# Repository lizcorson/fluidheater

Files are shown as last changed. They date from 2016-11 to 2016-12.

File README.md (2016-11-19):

# fluidheater
A small heater for flowing fluids.

## About
This is a project I'm working on for grad school. My goal is to heat flowing buffer fluid to skin temperature.

## Parts

* [Adafruit Feather 32u4 Basic Proto](http://www.digikey.com/product-search/en?keywords=1528-1514-ND)
* [Featherwing Proto](http://www.digikey.com/product-search/en?keywords=1528-1622-ND)
* [MOSFET](http://www.digikey.com/product-search/en?keywords=IRLB8721PBF-ND)
* [MAX31855 board](http://www.digikey.com/product-search/en?keywords=1528-1000-ND)
* [5V DC adapter](http://www.digikey.com/product-search/en?keywords=237-1385-ND)
* [Panel mount DC jack](http://www.digikey.com/product-search/en?keywords=CP-5-ND)
* [UM232R board](http://www.mouser.com/ProductDetail/FTDI/UM232R/)
* Male and female headers
* 1k resistor
* [Nichrome resistance heating wire, 30 AWG, p/n NI60-10-50](http://www.omega.com/pptst/NI60.html)
* [Type K 30 AWG thermocouple from Omega, SC-TT-K-30-36](http://www.omega.com/pptst/5LSC_5SRTC.html)
* [1/8" OD stainless tube (McMaster-Carr p/n 89895K712)](https://www.mcmaster.com/#catalog/122/148/=14vfa54)
* Swagelok fittings: 2x 1/16" port connector (SS-101-PC), 2x 1/8" to 1/16" reducing union (SS-200-6-1)

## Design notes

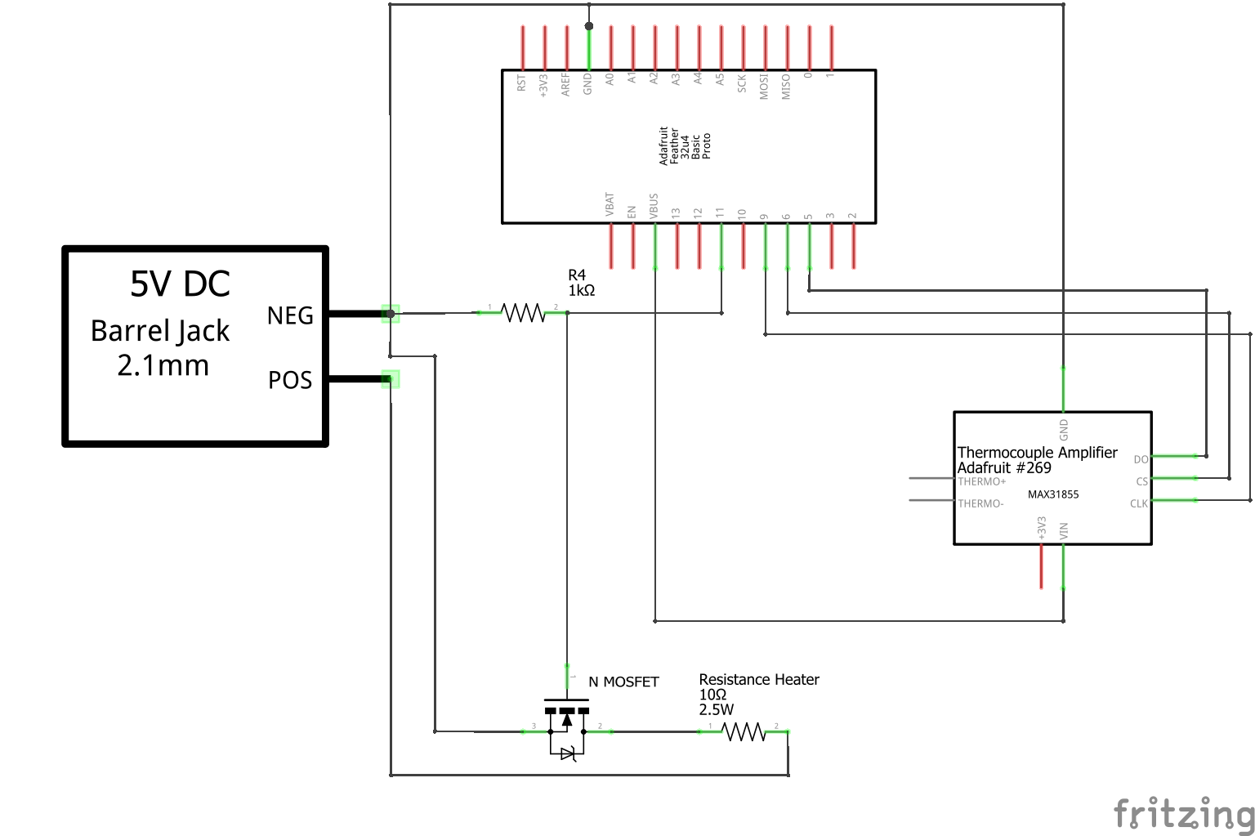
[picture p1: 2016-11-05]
schematics/heater schematic.png

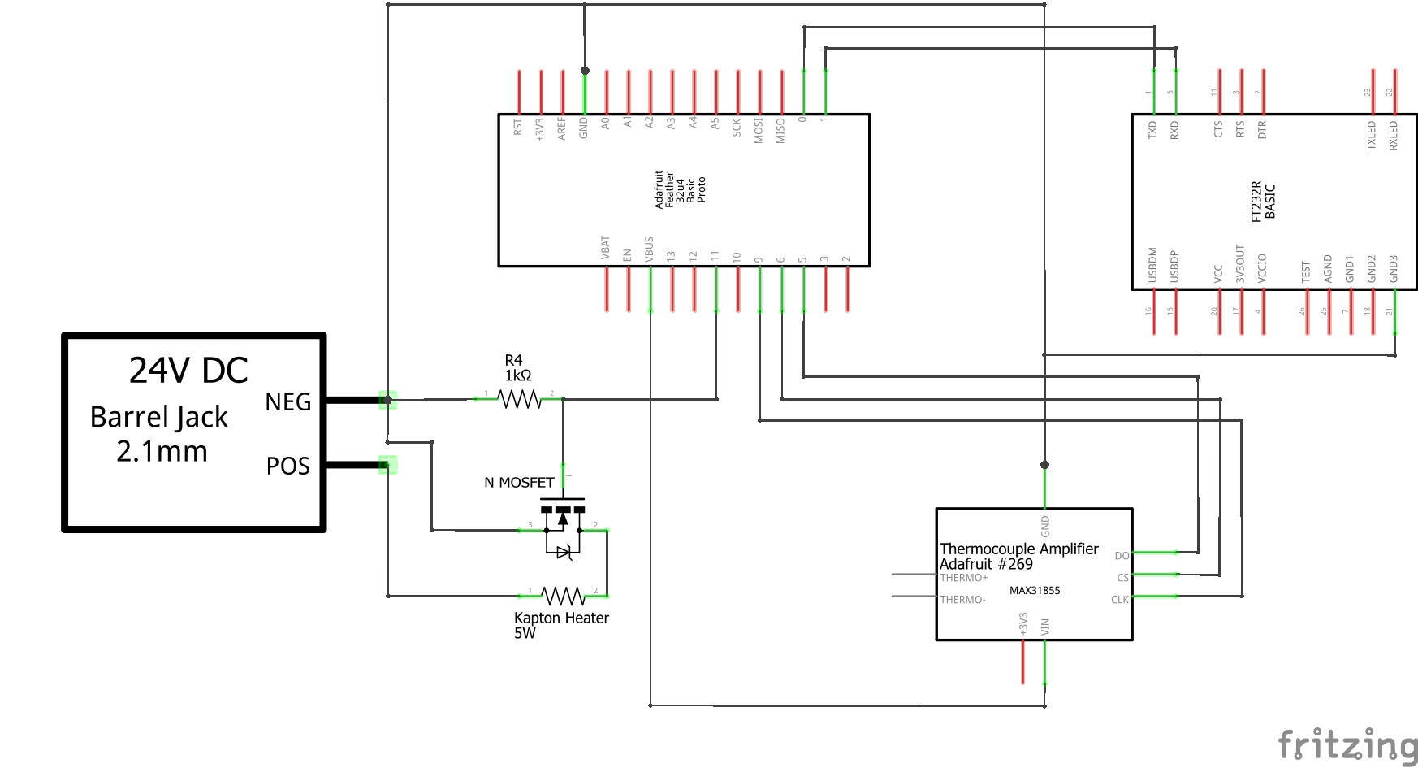
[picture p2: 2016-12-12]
schematics/heater schematic - kapton heater.png

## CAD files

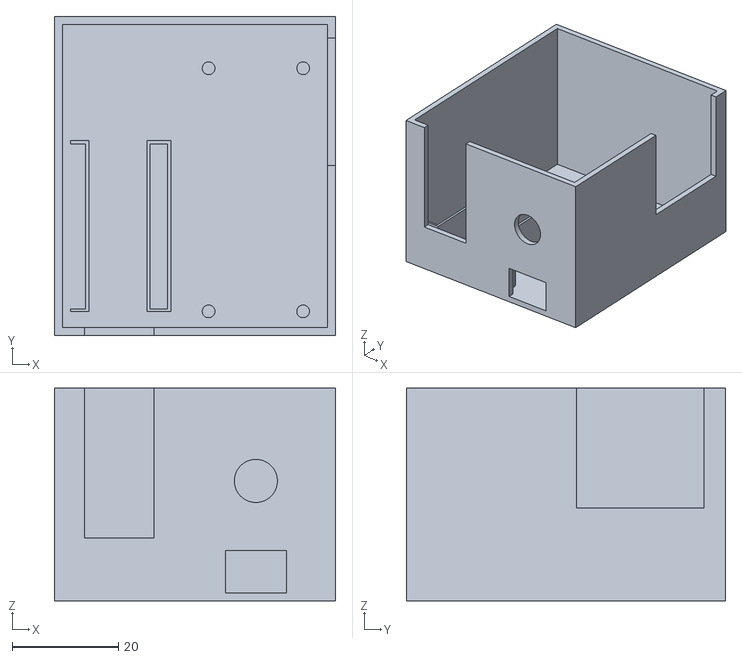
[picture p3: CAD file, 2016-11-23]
3dmodels/new case bottom.stl
52.9 x 60.0 x 40.0

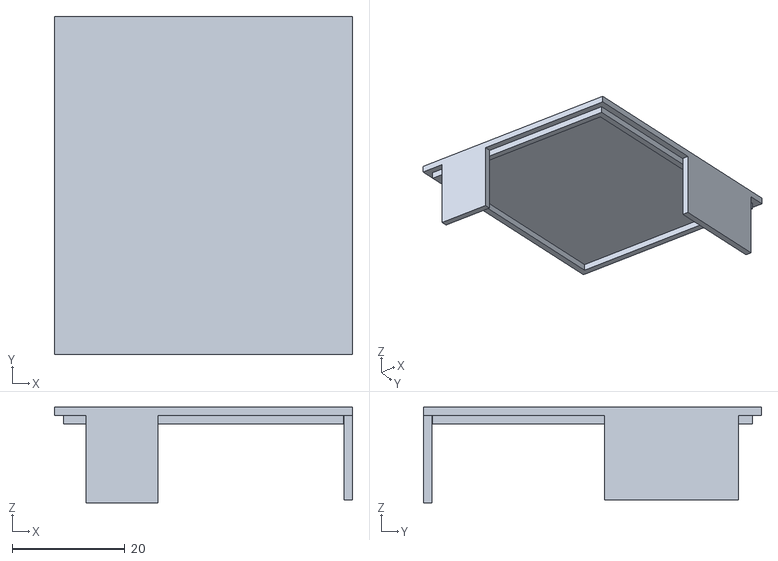
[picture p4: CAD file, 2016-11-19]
3dmodels/new case top.stl
52.9 x 60.0 x 17.0

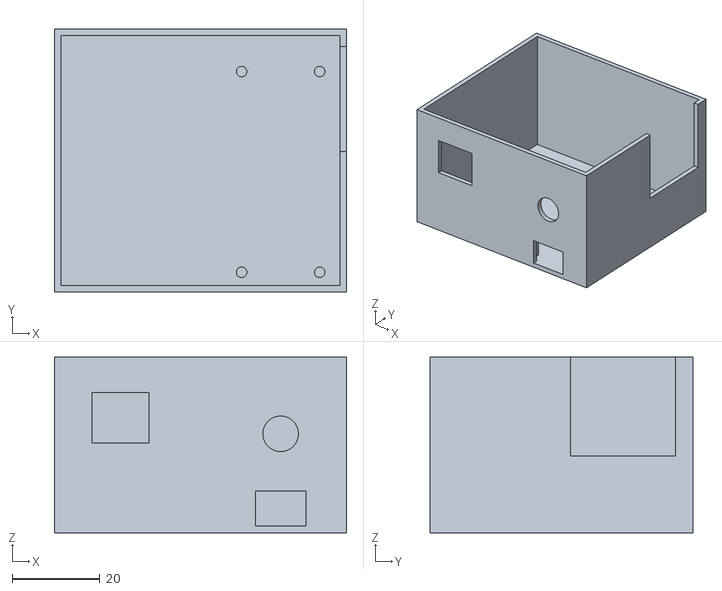
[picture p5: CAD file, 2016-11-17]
3dmodels/wide case bottom.stl
66.5 x 60.0 x 40.0

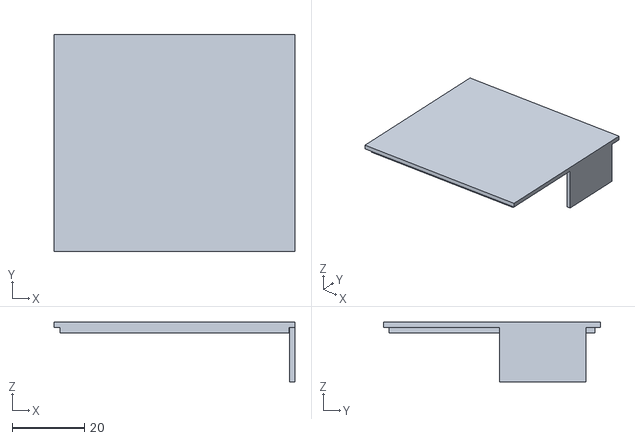
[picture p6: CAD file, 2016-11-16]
3dmodels/wide case top.stl
66.5 x 60.0 x 16.5

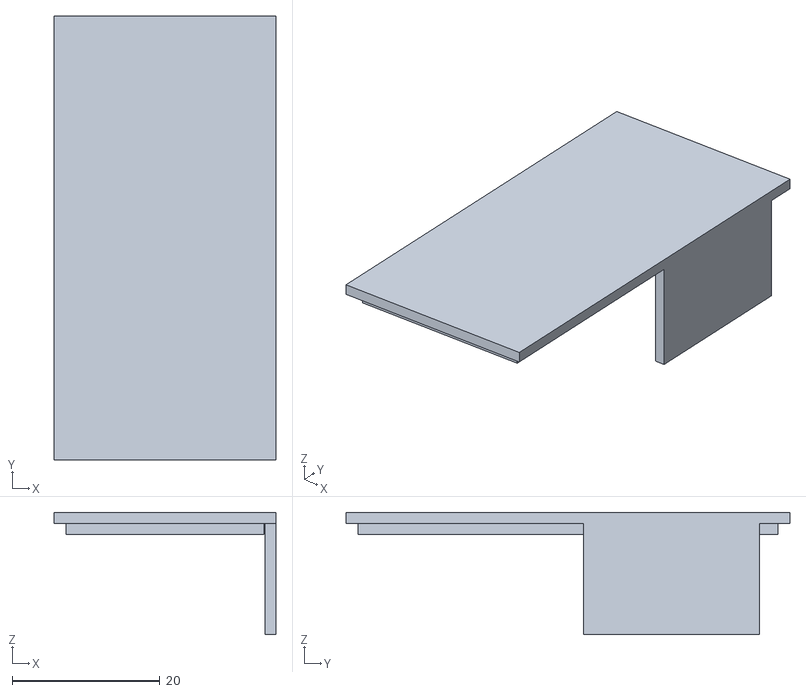
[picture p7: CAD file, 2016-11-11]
3dmodels/heater case top.stl
30.0 x 60.0 x 16.5

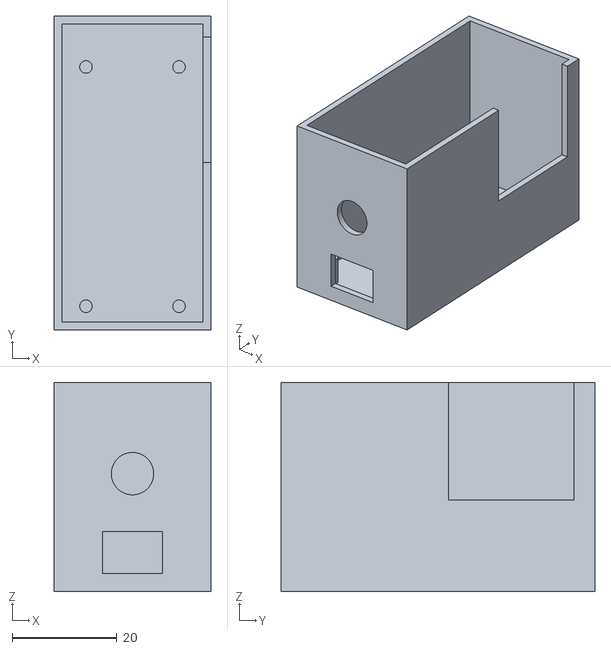
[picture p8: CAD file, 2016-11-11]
3dmodels/heater case bottom.stl
30.0 x 60.0 x 40.0

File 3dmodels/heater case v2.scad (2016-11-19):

wallthick = 1.5;

peg_r = 2.4/2;
peg_placelow = 0;
peg_placehigh = peg_placelow + 45.72;
fnval = 100;
peg_h = 6;
peg_spread = 17.78;

case_bottom_width = 30;
case_bottom_depth = 60;
case_bottom_height = 40;

pegs_xtranslate = (case_bottom_width-peg_spread)/2;
//pegs_ytranslate = 
//pegs_ztranslate = 

feather_depth = 50.8;
feather_width = 22.86;
feather_height = 1;

feather_xtranslate = (case_bottom_width-feather_width)/2;
feather_ytranslate = wallthick+.5;
feather_ztranslate = wallthick+1;


tc_cutout_xtranslate = case_bottom_width-wallthick;
tc_cutout_ytranslate = feather_ytranslate+30;
tc_cutout_ztranslate = wallthick+16;


tc_cutout_width = wallthick;
tc_cutout_depth = 24;
tc_cutout_height = case_bottom_height-tc_cutout_ztranslate;

tc_cover_height = 15;

usb_width = 11.5;
usb_height = 8;
usb_depth = wallthick;

usb_xtranslate = (case_bottom_width-usb_width)/2;
usb_ytranslate = 0;
usb_ztranslate = wallthick;

dcjack_r = 8.1/2;

dcjack_xtranslate = (case_bottom_width-2*dcjack_r)/2+dcjack_r;
dcjack_ytranslate = 0;
dcjack_ztranslate = feather_ztranslate+16+dcjack_r;

tolerance = .1;

boardwidth = 33.5;
boarddepth = 49;
boardheight = 1.2;
boardoffsety = 5;
usb2width = 13;
usb2height = 11.5;
usb2x = -15-usb2width;
usb2y = 0;
usb2z = 19+wallthick;

leftcasewidth = boardwidth + 3;
leftcasedepth = case_bottom_depth;
leftcaseheight = case_bottom_height;

*case_bottom();
case_top();

*translate([-boardwidth,boardoffsety,0]) cube([boardwidth,boarddepth,boardheight]);

module case_bottom() {
    union() {
        leftcase();
        rightcase();
    }
}

module leftcase() {
    difference () {
        translate([-leftcasewidth,0,0]) cube([leftcasewidth,leftcasedepth,leftcaseheight],center=false);
        translate([-leftcasewidth+wallthick,wallthick,wallthick]) cube([leftcasewidth-wallthick*2,leftcasedepth-wallthick*2,leftcaseheight],center=false);
        translate([-wallthick,wallthick,wallthick]) cube([wallthick,case_bottom_depth-wallthick*2,case_bottom_height]);
        translate([usb2x,usb2y,usb2z]) cube([usb2width,wallthick,usb2height]);
        
    }
}


module case_top() {
    //top
    translate([-leftcasewidth,0,case_bottom_height]) cube([case_bottom_width+leftcasewidth,case_bottom_depth,wallthick], center=false);
    
    //side panel
    translate([case_bottom_width-wallthick,tc_cutout_ytranslate+tolerance,case_bottom_height-tc_cover_height]) cube([wallthick,tc_cutout_depth-tolerance*2,tc_cover_height], center=false);
    
    //underneath
    translate([0,wallthick+tolerance,case_bottom_height-wallthick]) cube([case_bottom_width-wallthick-tolerance,case_bottom_depth-wallthick*2-tolerance*2,wallthick], center=false);
    translate([-leftcasewidth+wallthick+tolerance,wallthick+tolerance,case_bottom_height-wallthick]) cube([leftcasewidth-wallthick-tolerance,case_bottom_depth-wallthick*2-tolerance*2,wallthick], center=false);
}

module rightcase() {
    difference() {
        cube([case_bottom_width,case_bottom_depth,case_bottom_height], center=false);
        translate([wallthick,wallthick,wallthick]) cube([case_bottom_width-2*wallthick,case_bottom_depth-2*wallthick,case_bottom_height], center=false);
        translate([tc_cutout_xtranslate,tc_cutout_ytranslate,tc_cutout_ztranslate]) cube([tc_cutout_width,tc_cutout_depth,tc_cutout_height], center=false);
        translate([usb_xtranslate,usb_ytranslate,usb_ztranslate]) cube([usb_width, usb_depth, usb_height],center=false);
        translate([dcjack_xtranslate,dcjack_ytranslate,dcjack_ztranslate]) rotate([270,0,0]) cylinder(wallthick*1.1, dcjack_r, dcjack_r, false, $fn=fnval);
        translate([0,wallthick,wallthick]) cube([wallthick,case_bottom_depth-wallthick*2,case_bottom_height]);
    }
    translate([(case_bottom_width-peg_spread)/2,feather_ytranslate+2.54,0]) pegs();
}


*translate([feather_xtranslate,feather_ytranslate,feather_ztranslate]) feather();

module pegs() {
    translate([0,peg_placelow,wallthick])cylinder(peg_h, peg_r, peg_r, false, $fn=fnval);
    translate([peg_spread,peg_placelow,wallthick]) cylinder(peg_h, peg_r, peg_r, false, $fn=fnval);

    translate([0,peg_placehigh,wallthick])cylinder(peg_h, peg_r, peg_r, false, $fn=fnval);
    translate([peg_spread,peg_placehigh,wallthick]) cylinder(peg_h, peg_r, peg_r, false, $fn=fnval);
}

module feather() {
    cube([feather_width, feather_depth, feather_height], center = false);
}

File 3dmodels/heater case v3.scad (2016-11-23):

wallthick = 1.5;

peg_r = 2.4/2;
peg_placelow = 0;
peg_placehigh = peg_placelow + 45.72;
fnval = 100;
peg_h = 6;
peg_spread = 17.78;

case_bottom_width = 30;
case_bottom_depth = 60;
case_bottom_height = 40;

pegs_xtranslate = (case_bottom_width-peg_spread)/2;
//pegs_ytranslate = 
//pegs_ztranslate = 

feather_depth = 50.8;
feather_width = 22.86;
feather_height = 1;

um232_width = 17.9;
um232_depth = 38;
um232_height = 1.6;
um232_offset_x = -2;

u_usb_height = 10.7;
u_usb_width = 12;
u_usb_depth = 16.2;
u_usb_offset_y = -8;
u_usb_offset_x = 3.2;

uheader_height = 8.7;
uheader_depth = 30.2;
uheader_width = 2.5;
uheader_offset_y = 3.9;
uheader_offset_x1 = 0;
uheader_offset_x2 = um232_width - uheader_width;

feather_xtranslate = (case_bottom_width-feather_width)/2;
feather_ytranslate = wallthick+.5;
feather_ztranslate = wallthick+1;


tc_cutout_xtranslate = case_bottom_width-wallthick;
tc_cutout_ytranslate = feather_ytranslate+30;
tc_cutout_ztranslate = wallthick+16;


tc_cutout_width = wallthick;
tc_cutout_depth = 24;
tc_cutout_height = case_bottom_height-tc_cutout_ztranslate;

tc_cover_height = 15;

usb_width = 11.5;
usb_height = 8;
usb_depth = wallthick;

usb_xtranslate = (case_bottom_width-usb_width)/2;
usb_ytranslate = 0;
usb_ztranslate = wallthick;

dcjack_r = 8.1/2;

dcjack_xtranslate = (case_bottom_width-2*dcjack_r)/2+dcjack_r;
dcjack_ytranslate = 0;
dcjack_ztranslate = feather_ztranslate+16+dcjack_r;

tolerance = .1;

boardwidth = 33.5;
boarddepth = 49;
boardheight = 1.2;
boardoffsety = 5;
usb2width = 13;
usb2height = u_usb_height+(case_bottom_height-um232_height-uheader_height);
usb2x = -usb2width-u_usb_offset_x+um232_offset_x+1;
usb2y = 0;
usb2z = uheader_height+um232_height+wallthick;

leftcasewidth = um232_width + 5;
leftcasedepth = case_bottom_depth;
leftcaseheight = case_bottom_height;

module um232() {
    cube([um232_width,um232_depth,um232_height]);
    translate([u_usb_offset_x,u_usb_offset_y,um232_height]) cube([u_usb_width,u_usb_depth,u_usb_height]);
    translate([uheader_offset_x1,uheader_offset_y,-uheader_height]) cube([uheader_width,uheader_depth,uheader_height]);
    translate([uheader_offset_x2,uheader_offset_y,-uheader_height]) cube([uheader_width,uheader_depth,uheader_height]);
}

case_bottom();
*case_top();

shell_width = 1;
*translate([-um232_width+um232_offset_x,wallthick+tolerance,uheader_height+wallthick]) um232();

module um232holder() {
    difference() {
        color([1,0,0]) translate([um232_offset_x-um232_width+uheader_offset_x2-shell_width,uheader_offset_y+tolerance+wallthick-shell_width,wallthick]) cube([uheader_width+shell_width*2,uheader_depth+shell_width*2,uheader_height]);
        translate([uheader_offset_x2-um232_width+um232_offset_x-tolerance*4,uheader_offset_y+wallthick-tolerance*4,-uheader_height+uheader_height+wallthick]) cube([uheader_width+tolerance*8,uheader_depth+tolerance*8,uheader_height]);
    }
    difference() {
        color([1,0,0]) translate([um232_offset_x-um232_width+uheader_offset_x1,uheader_offset_y+tolerance+wallthick-shell_width,wallthick]) cube([uheader_width+shell_width,uheader_depth+shell_width*2,uheader_height]);
        translate([uheader_offset_x1-um232_width+um232_offset_x,uheader_offset_y+wallthick-tolerance*4,-uheader_height+uheader_height+wallthick]) cube([uheader_width+tolerance*4,uheader_depth+tolerance*8,uheader_height]); 
    }
}



*translate([-boardwidth,boardoffsety,0]) cube([boardwidth,boarddepth,boardheight]);

module case_bottom() {
    union() {
        leftcase();
        rightcase();
        um232holder();
    }
}

module leftcase() {
    difference () {
        translate([-leftcasewidth,0,0]) cube([leftcasewidth,leftcasedepth,leftcaseheight],center=false);
        translate([-leftcasewidth+wallthick,wallthick,wallthick]) cube([leftcasewidth-wallthick*2,leftcasedepth-wallthick*2,leftcaseheight],center=false);
        translate([-wallthick,wallthick,wallthick]) cube([wallthick,case_bottom_depth-wallthick*2,case_bottom_height]);
        translate([usb2x,usb2y,usb2z]) cube([usb2width,wallthick,usb2height]);
        
    }
}


module case_top() {
    //top
    translate([-leftcasewidth,0,case_bottom_height]) cube([case_bottom_width+leftcasewidth,case_bottom_depth,wallthick], center=false);
    
    //side panel
    translate([case_bottom_width-wallthick,tc_cutout_ytranslate+tolerance,case_bottom_height-tc_cover_height]) cube([wallthick,tc_cutout_depth-tolerance*2,tc_cover_height], center=false);
    
    //underneath -- got rid of most of this to reduce material used
    difference () {
        translate([0,wallthick+tolerance,case_bottom_height-wallthick]) cube([case_bottom_width-wallthick-tolerance,case_bottom_depth-wallthick*2-tolerance*2,wallthick], center=false);
        translate([0,wallthick*2+tolerance,case_bottom_height-wallthick]) cube([case_bottom_width-wallthick*2-tolerance,case_bottom_depth-wallthick*4-tolerance*2,wallthick], center=false);
    }
    difference() {
        translate([-leftcasewidth+wallthick+tolerance,wallthick+tolerance,case_bottom_height-wallthick]) cube([leftcasewidth-wallthick-tolerance,case_bottom_depth-wallthick*2-tolerance*2,wallthick], center=false);
        translate([-leftcasewidth+wallthick*2+tolerance,wallthick*2+tolerance,case_bottom_height-wallthick]) cube([leftcasewidth-wallthick*2-tolerance,case_bottom_depth-wallthick*4-tolerance*2,wallthick], center=false);
    }
    
    //usb cover
    cutout_height = case_bottom_height-wallthick-um232_height-uheader_height-u_usb_height-2;
    translate([usb2x-tolerance,0,case_bottom_height-cutout_height]) cube([usb2width-tolerance*2,wallthick,cutout_height]);
    
}

module rightcase() {
    difference() {
        cube([case_bottom_width,case_bottom_depth,case_bottom_height], center=false);
        translate([wallthick,wallthick,wallthick]) cube([case_bottom_width-2*wallthick,case_bottom_depth-2*wallthick,case_bottom_height], center=false);
        translate([tc_cutout_xtranslate,tc_cutout_ytranslate,tc_cutout_ztranslate]) cube([tc_cutout_width,tc_cutout_depth,tc_cutout_height], center=false);
        translate([usb_xtranslate,usb_ytranslate,usb_ztranslate]) cube([usb_width, usb_depth, usb_height],center=false);
        translate([dcjack_xtranslate,dcjack_ytranslate,dcjack_ztranslate]) rotate([270,0,0]) cylinder(wallthick*1.1, dcjack_r, dcjack_r, false, $fn=fnval);
        translate([0,wallthick,wallthick]) cube([wallthick,case_bottom_depth-wallthick*2,case_bottom_height]);
    }
    translate([(case_bottom_width-peg_spread)/2,feather_ytranslate+2.54,0]) pegs();
}


*translate([feather_xtranslate,feather_ytranslate,feather_ztranslate]) feather();

module pegs() {
    translate([0,peg_placelow,wallthick])cylinder(peg_h, peg_r, peg_r, false, $fn=fnval);
    translate([peg_spread,peg_placelow,wallthick]) cylinder(peg_h, peg_r, peg_r, false, $fn=fnval);

    translate([0,peg_placehigh,wallthick])cylinder(peg_h, peg_r, peg_r, false, $fn=fnval);
    translate([peg_spread,peg_placehigh,wallthick]) cylinder(peg_h, peg_r, peg_r, false, $fn=fnval);
}

module feather() {
    cube([feather_width, feather_depth, feather_height], center = false);
}

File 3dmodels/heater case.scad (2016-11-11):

wallthick = 1.5;

peg_r = 2.4/2;
peg_placelow = 0;
peg_placehigh = peg_placelow + 45.72;
fnval = 100;
peg_h = 6;
peg_spread = 17.78;

case_bottom_width = 30;
case_bottom_depth = 60;
case_bottom_height = 40;

pegs_xtranslate = (case_bottom_width-peg_spread)/2;
//pegs_ytranslate = 
//pegs_ztranslate = 

feather_depth = 50.8;
feather_width = 22.86;
feather_height = 1;

feather_xtranslate = (case_bottom_width-feather_width)/2;
feather_ytranslate = wallthick+.5;
feather_ztranslate = wallthick+1;


tc_cutout_xtranslate = case_bottom_width-wallthick;
tc_cutout_ytranslate = feather_ytranslate+30;
tc_cutout_ztranslate = wallthick+16;


tc_cutout_width = wallthick;
tc_cutout_depth = 24;
tc_cutout_height = case_bottom_height-tc_cutout_ztranslate;

tc_cover_height = 15;

usb_width = 11.5;
usb_height = 8;
usb_depth = wallthick;

usb_xtranslate = (case_bottom_width-usb_width)/2;
usb_ytranslate = 0;
usb_ztranslate = feather_ztranslate+feather_height;

dcjack_r = 8.1/2;

dcjack_xtranslate = (case_bottom_width-2*dcjack_r)/2+dcjack_r;
dcjack_ytranslate = 0;
dcjack_ztranslate = feather_ztranslate+16+dcjack_r;

tolerance = .1;

*case_bottom();
case_top();

module case_top() {
    //top
    translate([0,0,case_bottom_height]) cube([case_bottom_width,case_bottom_depth,wallthick], center=false);
    
    //side panel
    translate([case_bottom_width-wallthick,tc_cutout_ytranslate+tolerance,case_bottom_height-tc_cover_height]) cube([wallthick,tc_cutout_depth-tolerance*2,tc_cover_height], center=false);
    
    //underneath
    translate([wallthick+tolerance,wallthick+tolerance,case_bottom_height-wallthick]) cube([case_bottom_width-wallthick*2-tolerance*2,case_bottom_depth-wallthick*2-tolerance*2,wallthick], center=false);
}

module case_bottom() {
    difference() {
        cube([case_bottom_width,case_bottom_depth,case_bottom_height], center=false);
        translate([wallthick,wallthick,wallthick]) cube([case_bottom_width-2*wallthick,case_bottom_depth-2*wallthick,case_bottom_height], center=false);
        translate([tc_cutout_xtranslate,tc_cutout_ytranslate,tc_cutout_ztranslate]) cube([tc_cutout_width,tc_cutout_depth,tc_cutout_height], center=false);
        translate([usb_xtranslate,usb_ytranslate,usb_ztranslate]) cube([usb_width, usb_depth, usb_height],center=false);
        translate([dcjack_xtranslate,dcjack_ytranslate,dcjack_ztranslate]) rotate([270,0,0]) cylinder(wallthick*1.1, dcjack_r, dcjack_r, false, $fn=fnval);
    }
    translate([(case_bottom_width-peg_spread)/2,feather_ytranslate+2.54,0]) pegs();
}


*translate([feather_xtranslate,feather_ytranslate,feather_ztranslate]) feather();

module pegs() {
    translate([0,peg_placelow,wallthick])cylinder(peg_h, peg_r, peg_r, false, $fn=fnval);
    translate([peg_spread,peg_placelow,wallthick]) cylinder(peg_h, peg_r, peg_r, false, $fn=fnval);

    translate([0,peg_placehigh,wallthick])cylinder(peg_h, peg_r, peg_r, false, $fn=fnval);
    translate([peg_spread,peg_placehigh,wallthick]) cylinder(peg_h, peg_r, peg_r, false, $fn=fnval);
}

module feather() {
    cube([feather_width, feather_depth, feather_height], center = false);
}

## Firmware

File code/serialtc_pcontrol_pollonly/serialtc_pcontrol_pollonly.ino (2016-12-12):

#include <SPI.h>
#include <PID_v1.h>
#include "Adafruit_MAX31855.h"

// Connect to thermocouple instance with software SPI on any three
// digital IO pins.
#define MAXDO   5
#define MAXCS   6
#define MAXCLK  9

// initialize the Thermocouple
Adafruit_MAX31855 thermocouple(MAXCLK, MAXCS, MAXDO);

//heater control pin
#define HEATERPIN 11
#define MINTEMP 20
#define MAXTEMP 40

const int tempCheckDelay = 1000; // 1 second
long lastTCheck = 0;
//bool firstSend = false;
int heaterSetStatus = 0;
double heaterSetpoint = 20;
int heaterActive = 0;
int pwmOut = 0;
double tcRead = 0;

//PID
//Define Variables we'll be connecting to
double Setpoint, Input, Output;
double Kp = 175;
double Ki = 0;
double Kd = 0;
//Specify the links and initial tuning parameters
PID myPID(&Input, &Output, &Setpoint,Kp,Ki,Kd, DIRECT);

void setup() {
  Serial1.begin(38400);
  pinMode(HEATERPIN, OUTPUT);
  //turn the PID on
  myPID.SetMode(AUTOMATIC);  
}

void loop() {
  checkSerial();
  //Check temperature every tempCheckDelay ms
  if ((unsigned long)(millis() - lastTCheck) > tempCheckDelay) {
    double c = thermocouple.readCelsius();
    if (isnan(c)) {
     tcRead = -1; // so you know if there's a thermocouple error
    } else {
     Input = c;
     tcRead = c;
    }    
    lastTCheck = millis();
  }

  //manage heater
  if (heaterSetStatus == 1) { // if heater is active, output PWM based on PID
    Setpoint = (double)heaterSetpoint;
    myPID.Compute();
    pwmOut = (int)Output;
    analogWrite(HEATERPIN,pwmOut);
    //heater is only active if PWM > 0
    if (pwmOut > 0) {
      heaterActive = 1;
    } else {
      heaterActive = 0;
    }
  } else { // if heater is not active, output 0 on heater pin
    pwmOut = 0;
    analogWrite(HEATERPIN,pwmOut);
    heaterActive = 0;
  }
}

void checkSerial() {
  String inputString;
  if(Serial1.available() > 0) {
    inputString = Serial1.readStringUntil('\n');

    //expected message format is 1,35
    //on/off,temp set point (C)
    //parse message -- need some kind of error checking
    int delimIndex = inputString.indexOf(',');
    if (delimIndex >= 1) {
      String heaterString = inputString.substring(0,delimIndex);
      String setpointString = inputString.substring(delimIndex+1);
    
      int newHeaterStatus = heaterString.toInt();
      double newSetpoint = setpointString.toFloat();
      //Serial.println(newHeaterStatus);
      //sanity check data -- if it's okay, update global variables
      if (newHeaterStatus == 0 || newHeaterStatus == 1) {
        heaterSetStatus = newHeaterStatus;
        if (newSetpoint >= MINTEMP && newSetpoint <= MAXTEMP) {
          heaterSetpoint = newSetpoint;
        }
      }
    }
    else if (inputString.indexOf("POLL") >= 0) {
      //do nothing for now, just don't return
    }
    else {
      return; //return if invalid request
    }
    Serial1.println((String)tcRead + "," + (String)heaterActive + "," + (String)heaterSetStatus + "," + (String)heaterSetpoint + "," + (String)pwmOut);
    // Message output format: temperature reading,heater on/off status, heater on/off set, temperature set point,PWM output
    // Example: 36.5,1,1,35,81 
  } 
}

//Credit to Adafruit for MAX31855K examples!

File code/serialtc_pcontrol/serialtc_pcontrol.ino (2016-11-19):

#include <SPI.h>
#include <PID_v1.h>
#include "Adafruit_MAX31855.h"

// Connect to thermocouple instance with software SPI on any three
// digital IO pins.
#define MAXDO   5
#define MAXCS   6
#define MAXCLK  9

// initialize the Thermocouple
Adafruit_MAX31855 thermocouple(MAXCLK, MAXCS, MAXDO);

//heater control pin
#define HEATERPIN 11
#define MINTEMP 20
#define MAXTEMP 37

const int serialFrequency = 1000; // 1 second
long lastMessageSent = 0;
//bool firstSend = false;
int heaterSetStatus = 0;
int heaterSetpoint = 20;
int heaterActive = 0;
int pwmOut = 0;

//PID
//Define Variables we'll be connecting to
double Setpoint, Input, Output;
double Kp = 200;
double Ki = 0;
double Kd = 0;
//Specify the links and initial tuning parameters
PID myPID(&Input, &Output, &Setpoint,Kp,Ki,Kd, DIRECT);

void setup() {
  while (!Serial1); // wait for Serial on Leonardo/Zero, etc
  Serial1.begin(9600);
  //Serial1.println("MAX31855 test");
  // wait for MAX chip to stabilize
  delay(500); 
  pinMode(HEATERPIN, OUTPUT);
  //turn the PID on
  myPID.SetMode(AUTOMATIC);  
}

void loop() {
  checkSerial();
  //Send a serial message only once every serialFrequency ms
  if ((unsigned long)(millis() - lastMessageSent) > serialFrequency) {
    double c = thermocouple.readCelsius();
    if (isnan(c)) {
     Serial1.print("-1");
    } else {
     Serial1.print(c);
     Input = c;
    }
    Serial1.print(",");
    Serial1.print(heaterActive);
    Serial1.print(",");
    Serial1.print(heaterSetStatus);
    Serial1.print(",");
    Serial1.print(heaterSetpoint);   
    Serial1.print(",");
    Serial1.println(pwmOut);
    lastMessageSent = millis();
    // Message output format: temperature reading,heater on/off status, heater on/off set, temperature set point,PWM output
    // Example: 36.5,1,1,35,81 
  }

  //manage heater
  if (heaterSetStatus == 1) { // if heater is active, output PWM based on PID
    Setpoint = (double)heaterSetpoint;
    myPID.Compute();
    pwmOut = (int)(Output/2);
    analogWrite(HEATERPIN,pwmOut); //need to limit to a max of 128.
    //heater is only active if PWM > 0
    if (pwmOut > 0) {
      heaterActive = 1;
    } else {
      heaterActive = 0;
    }
  } else { // if heater is not active, output 0 on heater pin
    pwmOut = 0;
    analogWrite(HEATERPIN,pwmOut);
    heaterActive = 0;
  }
}

void checkSerial() {
  String inputString;
  if(Serial1.available() > 0) {
    inputString = Serial1.readStringUntil('\n');
    //expected message format is 1,35
    //on/off,temp set point (C)
    //parse message 
    int delimIndex = inputString.indexOf(',');
    String heaterString = inputString.substring(0,delimIndex);
    String setpointString = inputString.substring(delimIndex+1);
  
    int newHeaterStatus = heaterString.toInt();
    int newSetpoint = setpointString.toInt();
    //sanity check data -- if it's okay, update global variables
    if (newHeaterStatus == 0 || newHeaterStatus == 1) {
      heaterSetStatus = newHeaterStatus;
      if (newSetpoint >= MINTEMP && newSetpoint <= MAXTEMP) {
        heaterSetpoint = newSetpoint;
      }
    }
  } 
}

// Based on examples as below
/*************************************************** 
  This is an example for the Adafruit Thermocouple Sensor w/MAX31855K

  Designed specifically to work with the Adafruit Thermocouple Sensor
  ----> https://www.adafruit.com/products/269

  These displays use SPI to communicate, 3 pins are required to  
  interface
  Adafruit invests time and resources providing this open source code, 
  please support Adafruit and open-source hardware by purchasing 
  products from Adafruit!

  Written by Limor Fried/Ladyada for Adafruit Industries.  
  BSD license, all text above must be included in any redistribution
 ****************************************************/

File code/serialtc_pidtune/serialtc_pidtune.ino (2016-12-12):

#include <SPI.h>
#include <PID_v1.h>
#include "Adafruit_MAX31855.h"

// Connect to thermocouple instance with software SPI on any three
// digital IO pins.
#define MAXDO   5
#define MAXCS   6
#define MAXCLK  9

// initialize the Thermocouple
Adafruit_MAX31855 thermocouple(MAXCLK, MAXCS, MAXDO);

//heater control pin
#define HEATERPIN 11
#define MINTEMP 20
#define MAXTEMP 40

const int serialFrequency = 1000; // 1 second
long lastMessageSent = 0;
//bool firstSend = false;
int heaterSetStatus = 0;
int heaterSetpoint = 20;
int heaterActive = 0;
int pwmOut = 0;

//PID
//Define Variables we'll be connecting to
double Setpoint, Input, Output;
double Kp = 2;
double Ki = 2;
double Kd = 1;

//Specify the links and initial tuning parameters
PID myPID(&Input, &Output, &Setpoint,Kp,Ki,Kd, DIRECT);

void setup() {
  while (!Serial); // wait for Serial on Leonardo/Zero, etc
  Serial.begin(9600);
  //Serial.println("MAX31855 test");
  // wait for MAX chip to stabilize
  delay(500); 
  pinMode(HEATERPIN, OUTPUT);
  //turn the PID on
  myPID.SetMode(AUTOMATIC);
}

void loop() {
  checkSerial();
  //Send a serial message only once every serialFrequency ms
  if ((unsigned long)(millis() - lastMessageSent) > serialFrequency) {
    double c = thermocouple.readCelsius();
    if (isnan(c)) {
     Serial.print("-1");
    } else {
     Serial.print(c);
     Input = c;
    }
    Serial.print(",");
    Serial.print(heaterActive);
    Serial.print(",");
    Serial.print(heaterSetStatus);
    Serial.print(",");
    Serial.print(heaterSetpoint);   
    Serial.print(",");
    Serial.print(pwmOut);
    Serial.print(",");
    Serial.print(Kp);
    Serial.print(","); 
    Serial.print(Ki);
    Serial.print(",");
    Serial.println(Kd);
    lastMessageSent = millis();
    // Message output format: temperature reading,heater on/off status, heater on/off set, temperature set point
    // Example: 36.5,0,1,35 
    // ^ Temperature reading is above set point so heater turns off
  }

  //manage heater
  if (heaterSetStatus == 1) {// && Input < (double)heaterSetpoint) {
    Setpoint = (double)heaterSetpoint;
    myPID.Compute();
    pwmOut = (int)Output;
    analogWrite(HEATERPIN,pwmOut); //need to limit to a max of 128.
    
    //heater is only active if PWM > 0
    if (pwmOut > 0) {
      heaterActive = 1;
    } else {
      heaterActive = 0;
    }
  } else {
    pwmOut = 0;
    analogWrite(HEATERPIN,pwmOut);
    heaterActive = 0;
  }
  
  

}
void checkSerial() {
  String inputString;
  if(Serial.available() > 0) {
    inputString = Serial.readStringUntil('\n');
    //Serial.print("NEW INPUT: ");
    //Serial.println(inputString);
  
    //expected message format is 1,35,2,5,1
    // heater on/off, Tset, Kp, Ki, Kd
    //parse message -- this is gross but should work
    int delimIndex1 = inputString.indexOf(',');
    int delimIndex2 = inputString.indexOf(',',delimIndex1+1);
    int delimIndex3 = inputString.indexOf(',',delimIndex2+1);
    int delimIndex4 = inputString.indexOf(',',delimIndex3+1);
    String heaterString = inputString.substring(0,delimIndex1);
    String setpointString = inputString.substring(delimIndex1+1,delimIndex2);
    String KpString = inputString.substring(delimIndex2+1,delimIndex3);
    String KiString = inputString.substring(delimIndex3+1,delimIndex4);
    String KdString = inputString.substring(delimIndex4+1);

    //Serial.println("PID VALS:" + KpString + "," + KiString + "," + KdString);
    //need to change this parsing to allow for additional comma delimited values
    
    int newHeaterStatus = heaterString.toInt();
    int newSetpoint = setpointString.toInt();
    //sanity check data -- if it's okay, update global variables
    if (newHeaterStatus == 0 || newHeaterStatus == 1) {
      heaterSetStatus = newHeaterStatus;
      if (newSetpoint >= MINTEMP && newSetpoint <= MAXTEMP) {
        heaterSetpoint = newSetpoint;
      }
    }
    
    double newKp = KpString.toFloat();
    double newKi = KiString.toFloat();
    double newKd = KdString.toFloat();
    /*Serial.print("PID VALS:");
    Serial.print(newKp);
    Serial.print(",");
    Serial.print(newKi);
    Serial.print(",");
    Serial.println(newKd);*/
    myPID.SetTunings(newKp, newKi, newKd);
    Kp = newKp;
    Ki = newKi;
    Kd = newKd;
    /*Serial.print("PID VALS:");
    Serial.print(Kp);
    Serial.print(",");
    Serial.print(Ki);
    Serial.print(",");
    Serial.println(Kd);*/
    
    
  } 
}

// Based on examples as below
/*************************************************** 
  This is an example for the Adafruit Thermocouple Sensor w/MAX31855K

  Designed specifically to work with the Adafruit Thermocouple Sensor
  ----> https://www.adafruit.com/products/269

  These displays use SPI to communicate, 3 pins are required to  
  interface
  Adafruit invests time and resources providing this open source code, 
  please support Adafruit and open-source hardware by purchasing 
  products from Adafruit!

  Written by Limor Fried/Ladyada for Adafruit Industries.  
  BSD license, all text above must be included in any redistribution
 ****************************************************/

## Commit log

2016-11-03 Case model v1
    [heater case bottom.stl, heater case top.stl, heater case.scad]
2016-11-03 Heater code with on/off control
    Just on/off control at a set PWM level for now - plan to add PID later, but this works.
2016-11-04 Case edit
    Adjusting usb/DC jack cutout dimensions slightly
    [heater case.scad]
2016-11-05 another case edit
    [heater case bottom.stl, heater case top.stl, heater case.scad]
2016-11-07 case edit
    yet another case edit. USB opening was slightly too high.
    [heater case bottom.stl, heater case.scad]
2016-11-11 Updated serial stream
    Now includes the actual on/off status of the heater
2016-11-11 case edit 11/10
    Increased size of USB jack cutout because plug wasn't quite plugging in.
    Decreased wall thickness. Added tolerances to case top.
    [heater case bottom.stl, heater case top.stl, heater case.scad]
2016-11-11 Labview interface
    Labview interface for controlling and monitoring heater
2016-11-11 case top adjustment
    Adjusted tolerance down because top did not snap in to bottom
    [heater case top.stl, heater case.scad]
2016-11-16 adding FT232RL
    I had to add an external FT232RL chip due to serial driver issues for
    Labview 7 to do serial communications. Case design edited to be wider
    and have additional USB port. Also started playing with PID control.
    [heater case v2.scad, wide case bottom.stl, wide case top.stl]
2016-11-17 Changed to Serial1
    Changed Arduino code to use Serial1 for hardware serial
    [heater case v2.scad, wide case bottom.stl]
2016-11-19 Update 11-19-16
    *tuned PID - labview and arduino code for this process included
    *serialtc_pcontrol - proportional control, closer to the real thing
    *removed u232r from protoboard and redesigned case
    [heater case v3.scad, new case bottom.stl, new case top.stl]
2016-11-19 more 11-19
    [heater case v2.scad]
2016-11-21 Update 11-20
    -Case edit - UM232R did not quite fit in channels. Increased tolerance.
    -New microcontroller code: only sends data in response to a sent
    setpoint
    [heater case v3.scad, new case bottom.stl]
2016-11-23 case update 11-22
    increasing tolerances again
    [heater case v3.scad, new case bottom.stl]
2016-12-12 Kapton heater update
    Updated code to accomodate heater change
